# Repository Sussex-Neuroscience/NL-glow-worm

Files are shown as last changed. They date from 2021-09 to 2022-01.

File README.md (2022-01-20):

# GlowWorm_Trackball&LEDstim
A tracking and stimulation system for glow worms

    Authors: A.S.D Fernandes, E. Moubarak, A.M. Chagas & J.E. Niven
    Aknowlegements: M.J.Y. Zimmermann

## Aims
This set-up was designed to investigate male glow-worms attraction to a stimulus that mimics the females' glow. The aim was to be able to do so in tethered animals, whose behavior could be recorded at all times. Furthermore, we intended to have the ability to fully control the stimulus position relative to the glow-worm, as well as other characteristics such as intensity (brightness) and the duration of presentation.

## Methodology

Insects were fixed on top of a walking platform, which consisted in a light polystyrene ball that seated on top of a cup-shaped structure. The cup was perforated at the centre, allowing for air to be pumped through. Thus, the light ball was supported by an air cushion and could, with very little friction, rotate as the glow-worm walked. The movements of the ball, and thus the fictive path of the glow-worm, were recorded by two optical mice sensors, placed close to the ball and orthogonally to each other (Figure 1). The optical mice x and y displacements were recorded by a computer, and were then analyzed in terms of translational and angular distance and velocity. 

The stimulus consisted on LEDs with similar wavelength as the female glow, displayed as an array that surrounded ~ 180° of the insect's lateral visual field. The LEDs were attached to a controller and their intensity and duration of presentation controlled and recorded (Figure 1).

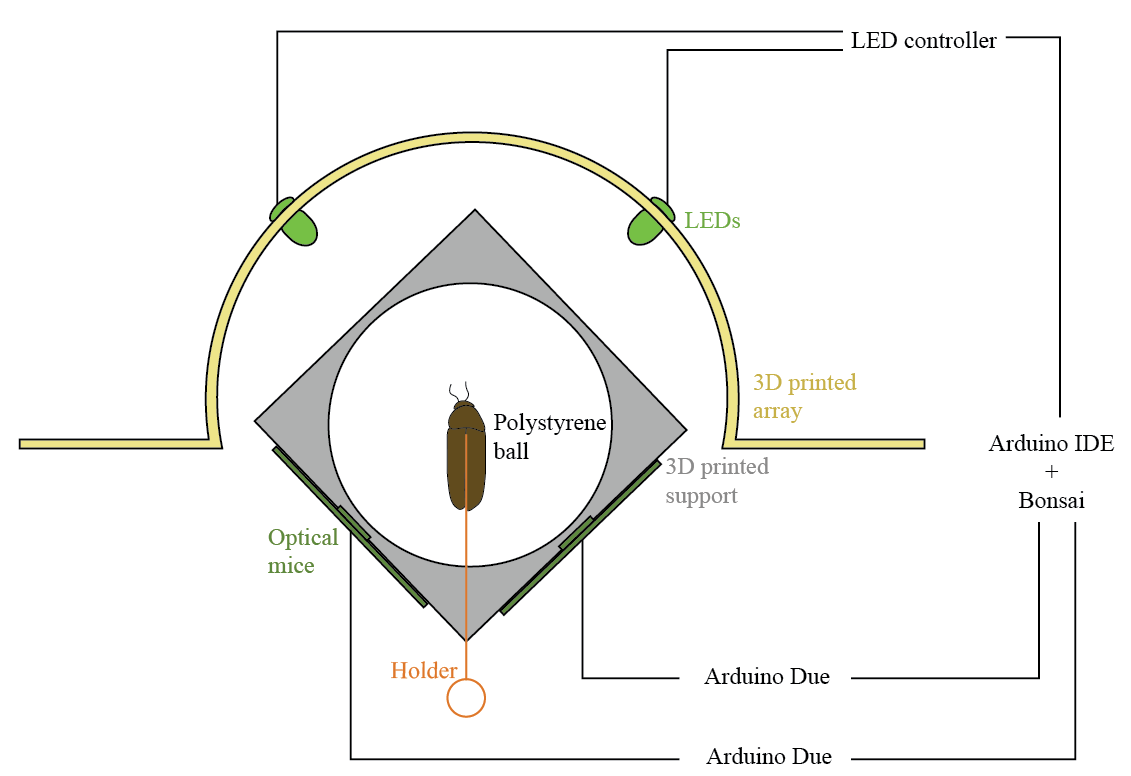
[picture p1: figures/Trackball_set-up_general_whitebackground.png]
Trackball schematics


**Figure 1: Schematics of trackball and stimulation set-up for glow-worms.** A tethered male glow-worm walks on top of a polystyrene ball supported by an air cushion which seats on a custom 3D printed support (gray). As the insect walks, the ball moves beneath it and its movements are recorded by two optical mice sensors (dark green). Each optical mouse is connected to an Arduino Due, in turn connected to a USB port. The glow-worm is presented with light stimuli through LEDs (light green) fixed to a custom 3D printed array (yellow) that surrounds ~ 180° of the insect's lateral visual field. The LEDs are attached to a controller, in turn connected to a USB port. The information from the LEDs and optical mice are recorded with Arduino IDE and saved with Bonsai software.

### Tethering 

Individual male glow-worms were tethered in a fixed position, not being allowed to rotate by themselves on top of the ball nor adjust their height (Figure 2A). The following material was needed for tethering:

- **Tube:** small tube (1.02mm ID, 1.98mm OD, 5mm length) glued to the wings, around the insect's center of mass, with rapid (5 seconds) UV glue. The tube was glued to the glow-worm at all times and attached to the experimental apparatus for experiments.

- **Pipette tip and syringe needle:** cut pipette tip glued to the bent tip of a long syringe needle (length: 120 mm), where the insect's tube could attach to.

- **Micromanipulator:** where the other end of the syringe needle could attach to, for allowing the experimenter to adjust the position and height of the insect on top of the ball.

### Trackball and support

The trackball system was composed of the following materials (Figure 2B,C):

- **Trackball:** polystyrene ball (5 cm diameter).

- **Support:** custom 3D printed structure (Trackball support scad).

- **Pump, regulator, system of tubes and connector:** the air flow was generated by a pump, regulated at about 2-5 lpm, and channeled to the support through a system of tubes of various sizes, ending with a specific connector that fits the model of the support.

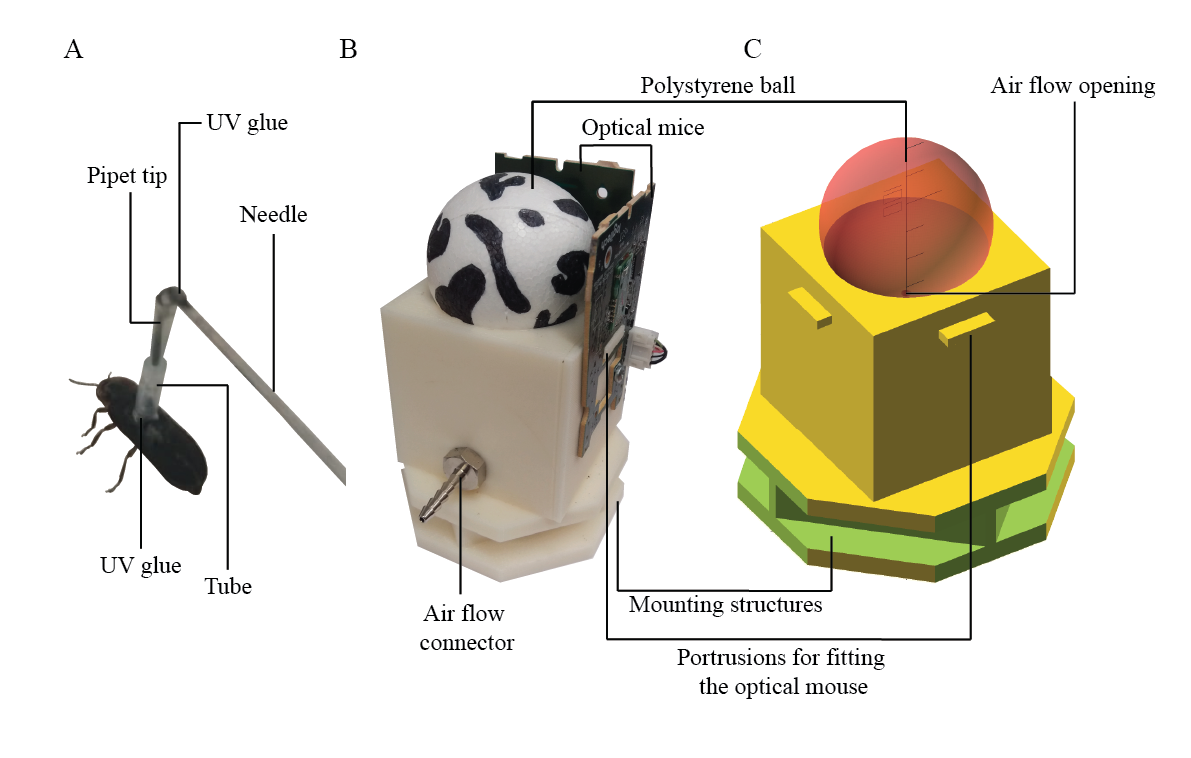
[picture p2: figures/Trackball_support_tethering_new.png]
Trackball support


**Figure 2: Detailed scheme of tethering and trackball support.** A) Male glow-worm with a tube glued to its wings, attached to the pipette tip glued to the bent end of the syringe. The syringe was attached to the micromanipulator for experiments (not shown). B) Photograph and C) Open Scad sketch of the trackball support with the real and fictive ball visible (respectively). The air flow entered through the connector on the side and passed through the opening at the center of the cup. The optical mice were fixed to the support through the portrusions on two ortogonal sides. The indents at the bottom of the support allowed for it to be mounted on a frame that kept it stable (not visible).

### Movement recordings

The walking behaviour of glow-worms was inferred by recordings of the trackball's movement. These recordings were acquired using the following hardware and software:

**Hardware**

- **Optic flow sensors:** two optical mice (M500 Logitech) sensors and relevant circuits were detached from the remaining parts. Each was attached to a side of the trackball support, orthogonal to each other, with the sensor at the level of the ball’s equator (Figure 2B).

- **Arduino Due:** each optical mouse was connected to one Arduino Due, which in turn connected to a USB port on a computer.

**Additional recordings** 

- **Infra-red camera:** placed above the set-up and connected to the same computer via USB (not shown).  

**Software**

- **Arduino IDE (v1.8.15):** for recording the x and y displacements of the optical mice, at ~ 60 fps (Mouse recorder arduino).

- **Bonsai (Lopes et al., 2015):** for saving the information from the Arduinos and camera, with a time stamp per frame, in a .csv file each (Bonsai mouse and cam).

### Stimulus 

A light stimulus was presented to the fixed glow-worm using the following (Figure 3):

**Hardware**

- **LEDs:** wavelength 555 nm; 5 mm diameter.

- **LED array:** custom 3D printed semicircular structure fitting up to 9 LEDs (LED array scad; Figure 3A), placed around the trackball apparatus.

- **LED controller:** custom-printed circuit board which accommodates the microcontroller, the LED driver and up to 24 LED channels (Figure 3B). You can find more detailed information on [BadenLab/LED-Zappelin](https://github.com/BadenLab/LED-Zappelin).

**Software**

- **Arduino IDE (v1.8.15):** for setting and recording the LEDs' intensity and duration (LED array arduino).

- **Bonsai (Lopes et al., 2015):** for saving the LED information and a time stamp per frame in a .csv file (Bonsai LEDs).

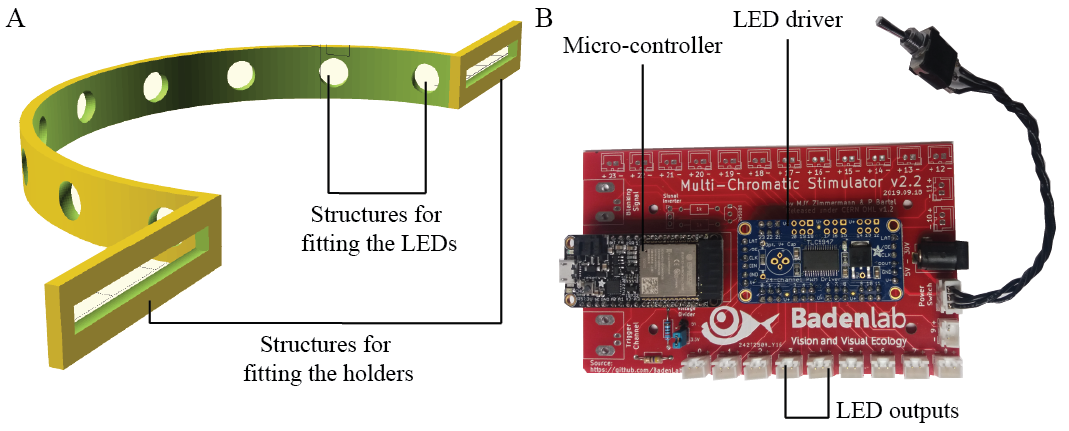
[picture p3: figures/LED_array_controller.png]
LED array and controller


**Figure 3: LED array and controller.** A) custom 3D printed array for fitting LEDs, with two side structures for mounting it on the same frame as the trackball support, arround it (not shown). B) Custom-printed circuit board which accommodates the microcontroller, the LED driver and up to 24 LED channels. 

You can find the detailed list of hardware and software here.

## Data analysis

### Raw variables from the optical mice

The optical mice (Logitech M500) comprise an infrared LED, an image acquisition system (IAS) and a digital signal processor (DSP). The infrared LED light projected onto the trackball surface bounces back and is captured by the IAS, which consists in a sensor that records, in this case, around 60 images per second. As the ball near the mouse moves, these images change and this change is processed by the DPS in order to determine the direction and magnitude of the movement. Thus, the raw data obtained from the optical mice, recorded by the Arduino Due and Bonsai, were:

- **x displacement:** specifies the relative change in pixels (dots/counts) between the current and previous frames, in the horizontal axis;

- **y displacement:** specifies the relative change in pixels (dots/counts) between the current and previous frames, in the vertical axis;

- **Time:** number of microseconds that have passed from the moment the program was uploaded into the Arduino Due.

These raw values were essentially distances, in pixel units, and each frame had an associated time.

### Specific experimental variables

The variable time was normalized to start at zero, converted to seconds (not shown), and used for merging the the data from the two mice to the nearest value. The **time difference** between frames was calculated as the difference between the current frame and the previous. 

For this particular set-up, the insect was tethered on top of the trackball facing a fixed direction. As the animal turned, the ball rotated underneath it and this movement was captured by changes in the horizontal axis of the optical mice sensors. If the animal turned 360 degrees, the ball moved the correspondent value on the opposite direction. Thus, the x displacement values, in pixel units, corresponded to the full perimeter of the ball at the equator level, at which the sensors were placed (Figure 4A).

The variables calculated from the x displacement were:

- **Mean x displacement:** the negative of the mean x displacement value of the two mice;

- **Angular displacement:** Mean x displacement divided by the ball radius and multiplied by 180/pi to obtain the angle in degrees (this also corresponds to instant heading or facing angle);

- **Cumulative angular displacement:** sum of angular displacement of current and all previous frames;

- **x velocity:** Mean x displacement divided by the time difference;

- **Angular velocity:** angular displacement divided by the time difference.

As the insect walked forwards on top of the ball, the movement was captured by the changes in the vertical axis of the optical mice sensors. Because the mice were orthogonal to each other, the y displacement from one mouse (the left) was taken as x and the y displacement from the other mouse as y. The forward velocity was calculated as the hypotenuse between the two sides (Figure 4B). Either mouse's y displacement could correspond to x or y.

The variables calculated from the y displacement were:

- **Forward displacement:** the squared root of the sum of the squared y displacement from one mouse and the squared y displacement of the other;

- **Cumulative forward displacement:** sum of forward displacement of current and all previous frames;

- **Forward velocity:** forward displacement divided by the time difference.

Lastly, the error between the two mice was calculated as the difference between their x displacement values, which should be the same if no error occurred.

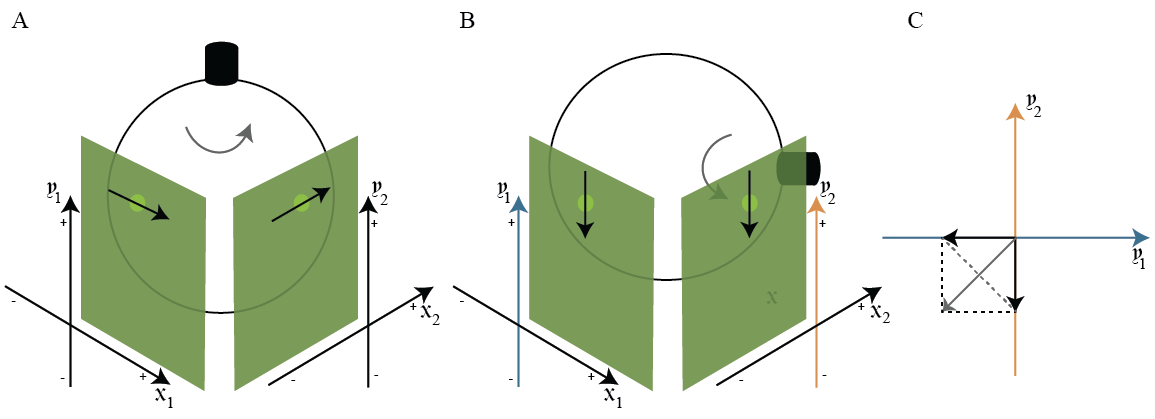
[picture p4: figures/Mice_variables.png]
Mice variables


**Figure 4: Movement direction and corresponding variables from optical mice.** A) Turning movement corresponds to rotation of the ball on the horizontal axis of the optical mice and, consequently, change in their x displacement values. The x displacement from both mice should have the same value if no recording error occured. B) Walking forward corresponds to rotation of the ball on the vertical axis of the optical mice and, consequently, change in their y displacement values. C) The real forward displacement is a combination of the y displacement values from both mice which, because they are ortogonal to each other, can be calculated as the hypotenuse between the two vectors.

## Calibration of the optical mice

### Stepper motor program

The calibration was performed using a stepper motor, controlled by an Arduino Uno. A custom 3D printed ball, of the same diameter of the polystyrene ball (5 cm), was attached to the motor and positioned on top of the trackball support. 

The motor and ball were aligned with the mice to create a fictive reading for:

- rotation on top of the ball (Figure 4A);

- translation forward (axis between the two mice; Figure 4B);

- translation to the left (aligned with the mouse on the right);

- translation to the right (aligned with the mouse on the left).

The motor and ball rotated 360 degrees 15 times, each time with a different speed, for each of the fictive readings.

### Calibration factor

The calibration factor was calculated by dividing the real distance moved, which corresponded to 15 times the perimeter of the ball at the equator (2 * pi * ball radius), by the mouse recorded total distance (x displacement and y displacement).

The calibration factor was very similar between the 4 tests, with a mean of 0.0291947 +/- 7.773015^{-4}.

This value must be multiplied by the x and y displacement from the mouse to get these and remaining variables in real distance and velocity values. This distance is in the unit specified in the ball radius (mm/cm and mm^2/cm^2, respectively).

You can find some semi-edited data from the trackball calibration here.

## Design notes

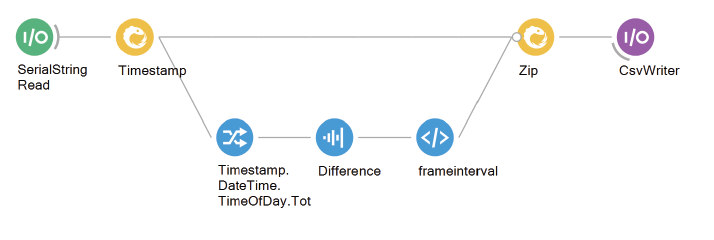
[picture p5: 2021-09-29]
figures/LED_bonsai.png

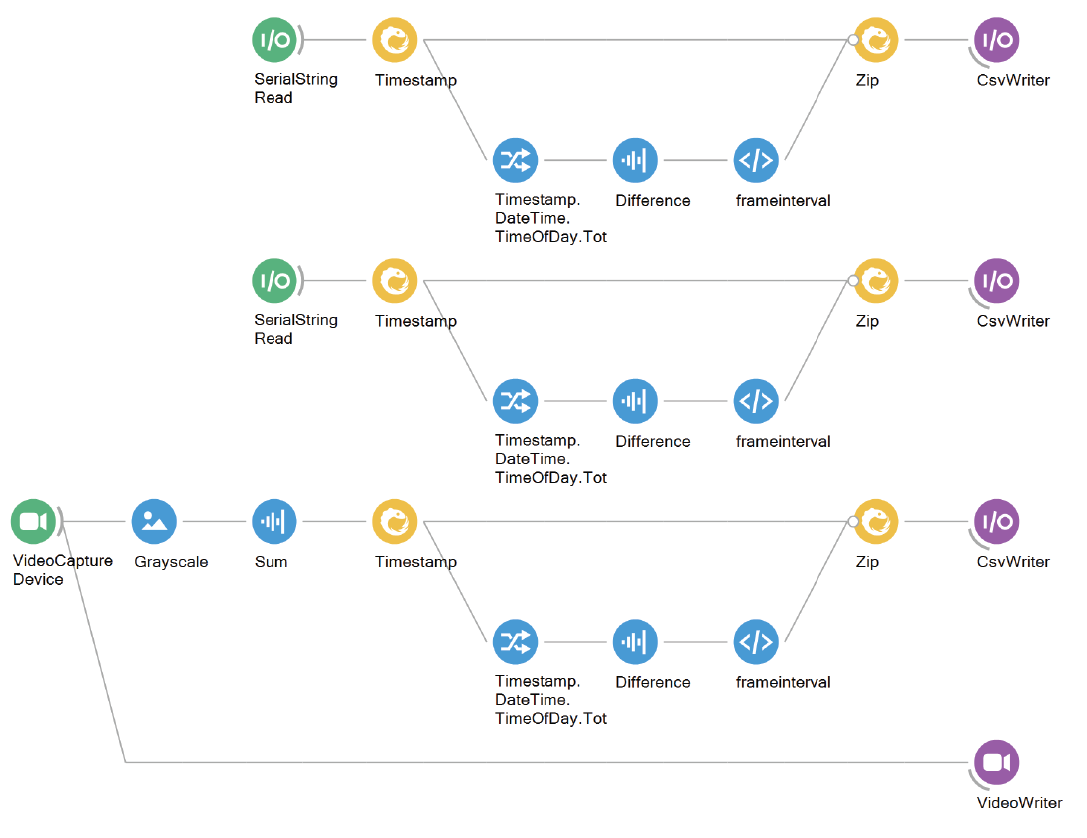
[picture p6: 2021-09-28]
figures/Bonsai_mice_cam.png

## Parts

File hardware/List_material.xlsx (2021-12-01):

Material | Description | Model | Brand | Link
Hardware
Trackball | Polystyrene, 5 cm diameter |  |  | https://ritohobby.co.uk/polystyrene/12200-white-polystyrene-ball-5cm-diameter-1-pcs-5700137321058.html
Trackball support | 3D printed (ABS filament)
Pump | Any with pressure > 10 lpm and constant flow | ET 80 Air Pump | Charles Austen | https://pumpwarehouse.co.uk/shop/charles-austen-et-80-air-pump/
Regulator | Any with pressure ~ 2-5 lpm |  | Futuris | https://www.amazon.co.uk/Futuris-CO2-Welding-Flowmeter-0-30lpm/dp/B01A8L5HYO
Air flow tubes | Any combination that fit the pump, regulator and adaptor
Air flow connector | 8 mm OD | 176-2014 | RS PRO | https://uk.rs-online.com/web/p/hose-connectors/1762014/?searchHistory=%7B%22enabled%22%3Atrue%7D
Optical mouse (2x) | Corded; Infra-red light | M500 | Logitech | https://www.logitech.com/en-us/products/mice/m500s-corded-mouse.910-005783.html
Camera | Infra-red, compatible with PC | ELP-USBFHD05MT-RL36-U | SHENZHEN AILIPU TECNHOLOGY | https://www.amazon.co.uk/gp/product/B015VE6MII/ref=ppx_yo_dt_b_asin_title_o09_s00?ie=UTF8&psc=1
LEDs | Wavelength: 555nm; Size: 5mm diameter | reference SSL-LX5093PGD | Mouser Electronics | https://www.mouser.co.uk/ProductDetail/Lumex/SSL-LX5093PGD?qs=dKJqHdD0tEBZaKNUwnw%2FQg%3D%3D
Arduino Due (2x) |  |  | Arduino | https://uk.rs-online.com/web/p/arduino/7697412/
USB to microUSB cables | Any microUSB male to microUSB male
USB to microUSB connector | Any USB male to microUSB female
Computer | 4 USB ports
LED array | 3D printed semi-circular structure
Microcontroller |  | 3405 | Adafruit Industries LLC | https://www.digikey.co.uk/en/products/detail/adafruit-industries-llc/3405/7244967?s=N4IgTCBcDaIIwFYwA4C0Y7LqgcgERAF0BfIA
LED driver |  | 1429 | Adafruit Industries LLC | https://www.digikey.co.uk/en/products/detail/adafruit-industries-llc/1429/5353645?s=N4IgTCBcDaIIwFYwA4C0c7IagcgERAF0BfIA
Circuit board | Custom-printed |  |  | https://github.com/BadenLab/LED-Zappelin
Frame | 10x10 mm | 100012 | MakerBeam | https://www.makerbeam.com/makerbeam-makerbeam-regular-starter-kit-black.html
Tube for tethering | 1.02mm ID 1.98mm OD | 800/100/300 | Smiths Medical™
Pipet for tethering | 200 ul; Polypropylene | 70.3030.020 | Sarstedt | https://www.sarstedt.com/en/products/laboratory/liquid-handling/pipette-tips/product/70.3030.020/
Syringe needle for tethering | 120 mm length; 0.8 mm OD | 466564/3 | B Braun™ | https://www.fishersci.co.uk/shop/products/stainless-chromium-nickel-steel-light-silicone-coating-needle/10438881
Micromanipulator for tethering | Any that fits the end of the syringe and allows fine adjustments
Software
Arduino IDE |  | Version 1.8.15 | Arduino | https://www.arduino.cc/en/Main/Software_
Bonsai |  |  |  | https://bonsai-rx.org/

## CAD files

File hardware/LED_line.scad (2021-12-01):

// This is a 9 cm diameter semicircular LED array that 
// fits 9 typical LEDs with 5 mm diameter
// equally spaced between each other
// with two holders on the side for attaching it to a frame

echo(version=version());
module LED_line()

// circular array  - 9 cm diameter

difference(){
   difference(){
        difference(){
        cylinder (h = 10, d = 94, $fn=200);
        translate([0, 0, -0.5]){cylinder (h = 11, d = 90, $fn=200);}
        }
        translate([5, -47, -0.5]){cube([120, 120, 120]);}
    }

// holes for LEDs
  // center  
   translate([-46,0,5]){sphere(d = 6, $fn = 50);}

  // side 1 
   translate([-42.498,17.603,5]){sphere(d = 6, $fn = 50);} 
   translate([-32.5269,32.5269,5]){sphere(d = 6, $fn = 50);} 
   translate([-17.603,42.498,5]){sphere(d = 6, $fn = 50);} 
   translate([0,46,5]){sphere(d = 6, $fn = 50);} 
   
  // side 2 
   translate([-42.498,-17.603,5]){sphere(d = 6, $fn = 50);} 
   translate([-32.5269,-32.5269,5]){sphere(d = 6, $fn = 50);} 
   translate([-17.603,-42.498,5]){sphere(d = 6, $fn = 50);} 
   translate([0,-46,5]){sphere(d = 6, $fn = 50);}    
}    

    
// holders    
difference(){
    translate([5,-80.5,0]){cube([2,36,10]);}
    translate([6,-48,5]){rotate([90,0,0]){cylinder(d = 4, h = 30, $fn = 50);}
}}

difference(){
    translate([5,44.5,0]){cube([2,36,10]);}
    translate([6,78,5]){rotate([90,0,0]){cylinder(d = 4, h = 30, $fn = 50);}}
//} 
}










LED_line();

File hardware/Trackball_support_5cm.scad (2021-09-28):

//module TrackBallSupport (h1,r1,z,r2,r3,a,a2,h2,r4,h3){

echo(version=version());
Trackball_support();

module Trackball_support(){



//------- Ball diameter - to change for specific ball size
    ball_diameter = 50;


//------- Other variables - optimized for optical mouse Logitech M500 - do not change unless using different sensor
    ball_to_edge = 5;
    support_cube = ball_diameter + (ball_to_edge*2);
    cup_size = support_cube + (ball_diameter/6);//1/3 of the ball

    mouse_piece_length_out = 5;
    mouse_piece_width = 3;
    mouse_piece_length = 16;
    mouse_to_top = 7;
    
//------- Base - optimized for fitting Makerbeam - do not change unless changing the set-up
    
    beam_width = 12;
    
    base_height = beam_width * 2;
    base_width = support_cube * 1.5;


difference(){ //for inlet

// Trackball support

translate([0,0,base_height]){
     difference(){ 
     difference(){
         translate([-support_cube/2,-support_cube/2,0]){cube(support_cube);}
         #translate([0,0,cup_size]){sphere(d=ball_diameter,$fn=200);} 
     }

 }
 }
 
 
// inlet for pump 
translate([0,0,base_height+10]){ 
 rotate([90,0,0]){
          translate([0,0,support_cube/2-9]){cylinder(h=10,d=9.8,$fn=30);}
          cylinder(h=support_cube/2+1,d=3, $fn=30);
          translate([0,-1.5,0]){rotate([-90,0,0]){cylinder(h=support_cube+1.5,d=3, $fn=30);}}
      }
  }
 }
 

// pieces for fitting mice  
  rotate([0,90,0]){translate([-(support_cube+base_height-mouse_to_top),-mouse_piece_length/2,support_cube/2]){cube([mouse_piece_width,mouse_piece_length,mouse_piece_length_out]);}}
  rotate([0,90,90]){translate([-(support_cube+base_height-mouse_to_top),-mouse_piece_length/2,support_cube/2]){cube([mouse_piece_width,mouse_piece_length,mouse_piece_length_out]);}}

 
// Base

difference(){

rotate([0,0,45]){
    difference(){
    
      translate([-base_width/2,-base_width/2,0]){cube([base_width,base_width,base_height]);}
  
      union(){
          rotate(90,0,0){translate([-(base_width/2),base_width/2-beam_width,beam_width/2]){cube([base_width,beam_width+0.1,beam_width]);}}
          rotate(90,0,0){translate([(-base_width/2),-base_width/2-0.1,beam_width/2]){cube([base_width,beam_width+0.1,beam_width]);}}
          rotate(0,90,0){translate([(-base_width/2),-base_width/2-0.1,beam_width/2]){cube([base_width,beam_width+0.1,beam_width]);}}
         rotate(0,90,0){translate([-(base_width/2),base_width/2-beam_width,beam_width/2]){cube([base_width,beam_width+0.1,beam_width]);}}
      
  }
  }
  }
  translate([-base_width/2,base_width/2,-1]){cube([base_width,base_width,base_height+1.5]);}
  translate([base_width/2,-base_width/2,-1]){cube([base_width,base_width,base_height+1.5]);}
  translate([-base_width*1.5,-base_width/2,-1]){cube([base_width,base_width,base_height+1.5]);}
  translate([-base_width/2,-base_width*1.5,-1]){cube([base_width,base_width,base_height+1.5]);}
} 

}

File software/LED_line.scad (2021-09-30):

// This is a 9 cm diameter semicircular LED array that 
// fits 9 typical LEDs with 5 mm diameter
// equally spaced between each other
// with two holders on the side for attaching it to a frame

echo(version=version());
module LED_line()

// circular array  - 9 cm diameter

difference(){
   difference(){
        difference(){
        cylinder (h = 10, d = 94, $fn=200);
        translate([0, 0, -0.5]){cylinder (h = 11, d = 90, $fn=200);}
        }
        translate([5, -47, -0.5]){cube([120, 120, 120]);}
    }

// holes for LEDs
  // center  
   translate([-46,0,5]){sphere(d = 6, $fn = 50);}

  // side 1 
   translate([-42.498,17.603,5]){sphere(d = 6, $fn = 50);} 
   translate([-32.5269,32.5269,5]){sphere(d = 6, $fn = 50);} 
   translate([-17.603,42.498,5]){sphere(d = 6, $fn = 50);} 
   translate([0,46,5]){sphere(d = 6, $fn = 50);} 
   
  // side 2 
   translate([-42.498,-17.603,5]){sphere(d = 6, $fn = 50);} 
   translate([-32.5269,-32.5269,5]){sphere(d = 6, $fn = 50);} 
   translate([-17.603,-42.498,5]){sphere(d = 6, $fn = 50);} 
   translate([0,-46,5]){sphere(d = 6, $fn = 50);}    
}    

    
// holders    
difference(){
    translate([5,-80.5,0]){cube([2,36,10]);}
    translate([6,-48,5]){rotate([90,0,0]){cylinder(d = 4, h = 30, $fn = 50);}
}}

difference(){
    translate([5,44.5,0]){cube([2,36,10]);}
    translate([6,78,5]){rotate([90,0,0]){cylinder(d = 4, h = 30, $fn = 50);}}
//} 
}










LED_line();

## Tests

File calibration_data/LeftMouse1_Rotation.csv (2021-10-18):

 | LeftMouse1_x | LeftMouse1_y | Time | Time_normalized | Time_normalized_seconds
1 | 0 | 0 | 3868477732 | 0 | 0
2 | 0 | 0 | 3868494372 | 16640 | 0.01664
3 | 0 | 0 | 3868511012 | 33280 | 0.03328
4 | 0 | 0 | 3868527652 | 49920 | 0.04992
5 | 0 | 0 | 3868544292 | 66560 | 0.06656
6 | 0 | 0 | 3868560932 | 83200 | 0.0832
7 | 0 | 0 | 3868577572 | 99840 | 0.09984
8 | 0 | 0 | 3868594212 | 116480 | 0.11648
9 | 0 | 0 | 3868610852 | 133120 | 0.13312
10 | 0 | 0 | 3868627492 | 149760 | 0.14976
11 | 0 | 0 | 3868644132 | 166400 | 0.1664
12 | 0 | 0 | 3868660772 | 183040 | 0.18304
13 | 0 | 0 | 3868677412 | 199680 | 0.19968
14 | 0 | 0 | 3868694052 | 216320 | 0.21632
15 | 0 | 0 | 3868710692 | 232960 | 0.23296
16 | 0 | 0 | 3868727332 | 249600 | 0.2496
17 | 0 | 0 | 3868743972 | 266240 | 0.26624
18 | 0 | 0 | 3868760612 | 282880 | 0.28288
19 | 0 | 0 | 3868777252 | 299520 | 0.29952
20 | 0 | 0 | 3868793892 | 316160 | 0.31616
21 | 0 | 0 | 3868810532 | 332800 | 0.3328
22 | 0 | 0 | 3868827172 | 349440 | 0.34944
23 | 0 | 0 | 3868843812 | 366080 | 0.36608
24 | 0 | 0 | 3868860452 | 382720 | 0.38272
25 | 0 | 0 | 3868877092 | 399360 | 0.39936
26 | 0 | 0 | 3868893732 | 416000 | 0.416
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

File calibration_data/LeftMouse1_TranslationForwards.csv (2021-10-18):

 | LeftMouse1_x | LeftMouse1_y | Time | Time_normalized | Time_normalized_seconds
1 | 0 | 0 | 143813412 | 0 | 0
2 | 0 | 0 | 143829012 | 15600 | 0.0156
3 | 0 | 0 | 143844612 | 31200 | 0.0312
4 | 0 | 0 | 143860212 | 46800 | 0.0468
5 | 0 | 0 | 143875812 | 62400 | 0.0624
6 | 0 | 0 | 143891412 | 78000 | 0.078
7 | 0 | 0 | 143907012 | 93600 | 0.0936
8 | 0 | 0 | 143922612 | 109200 | 0.1092
9 | 0 | 0 | 143938212 | 124800 | 0.1248
10 | 0 | 0 | 143953812 | 140400 | 0.1404
11 | 0 | 0 | 143969412 | 156000 | 0.156
12 | 0 | 0 | 143985012 | 171600 | 0.1716
13 | 0 | 0 | 144000612 | 187200 | 0.1872
14 | 0 | 0 | 144016212 | 202800 | 0.2028
15 | 0 | 0 | 144031812 | 218400 | 0.2184
16 | 0 | 0 | 144047412 | 234000 | 0.234
17 | 0 | 0 | 144063012 | 249600 | 0.2496
18 | 0 | 0 | 144078612 | 265200 | 0.2652
19 | 0 | 0 | 144094212 | 280800 | 0.2808
20 | 0 | 0 | 144109812 | 296400 | 0.2964
21 | 0 | 0 | 144125412 | 312000 | 0.312
22 | 0 | 0 | 144141012 | 327600 | 0.3276
23 | 0 | 0 | 144156612 | 343200 | 0.3432
24 | 0 | 0 | 144172212 | 358800 | 0.3588
25 | 0 | 0 | 144187812 | 374400 | 0.3744
26 | 0 | 0 | 144203412 | 390000 | 0.39
27 | 0 | 0 | 144219012 | 405600 | 0.4056
28 | 0 | 0 | 144234612 | 421200 | 0.4212
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

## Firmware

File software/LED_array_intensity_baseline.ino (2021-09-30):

// Initialise the LED controler
// For more information on the LED controler go to https://github.com/BadenLab/LED-Zappelin

#include <SPI.h>                            // Include the arduino serial port interface library
#include "Adafruit_TLC5947.h"               // Include the Adafruit TLC5947 libvrary. For better result one may change the number of channel defined in the Adafruit_TLC5947.cpp library
#include <SerialCommand.h> //library to tokenize serial commands  

#define   nDriver         1
#define   data           18             // SPI connection, DIN connected to pin MOSI/18
#define   clock           5             // SPI connection, CLK connected to pin SCK/5
#define   latch          21             // SPI connection, LAT connected to pin 21
#define   oe             25            // Optional feature to prevent LED to light up when powering up the TLC board connected to pin A1/DAC1
//const int      pSyncOut      =   26;    // Trigger channel must be connected to pin A0/DAC2
//const int      pBlank        =   36;    // Blanking signal channel must be connected to pin A4/36


SerialCommand sCmd;     // The demo SerialCommand object


Adafruit_TLC5947 tlc = Adafruit_TLC5947(nDriver, clock, data, latch);

int wait=500;

void setup() {
  
  // put your setup code here, to run once:


// Initialise the serial communication with PC
Serial.begin(9600);
// Initialise the Adafruit TLC driver 
tlc.begin();

pinMode(oe, OUTPUT);
digitalWrite(oe, LOW);

 
tlc.write();  
}


// Exemple experiment with two alternating LEDs, increasing in brightness

void loop() {

  int trials = 5;
  const int led_array[] = {4,5}; //LEDs number; note: the board starts counting leds from 0
  int led = led_array[random(0,2)]; //randomize which LED is first to be turned on
  const int brightness[] = {1,10,100,1000,4000}; //brightness levels

 // Print "Ready" at start of the experiment
 // and LED and Brightness = 0
 
      Serial.println("Ready");
      Serial.print(0); 
      Serial.print(";");
      Serial.print(0);
      Serial.print(";");
      Serial.println(micros());

  //turn all leds off
  for (int i=0; i<9; i++){
      tlc.setPWM(i,0);  
    }//end for
  tlc.write();
  delay(1000*60*5);//wait 5 min
      Serial.print(0);
      Serial.print(";");
      Serial.print(0);
      Serial.print(";");
      Serial.println(micros());

  // for loop quick switch + increase intensity every trial    
  for (int i=0; i<trials; i++){
      int bright = brightness[i];

  //turn all leds off
  for (int i=0; i<9; i++){
      tlc.setPWM(i,0);  
    }//end for
  tlc.write();
  
          tlc.setPWM(led,bright);
          tlc.write();
          delay(1000*20);
          Serial.print(led);
          Serial.print(";");
          Serial.print(bright);
          Serial.print(";");
          Serial.println(micros());


  
                if (led == 5) {
                          tlc.setPWM(4,bright);
                          tlc.write();
                           tlc.setPWM(led,0);
                           tlc.write();
                           delay(1000*20);
                            Serial.print(4);
                            Serial.print(";");
                            Serial.print(bright);
                            Serial.print(";");
                            Serial.println(micros());
                      }
                
                    
                      else if (led == 4){

                            tlc.setPWM(5,bright);
                            tlc.write();
                             tlc.setPWM(led,0);
                             tlc.write();
                             delay(1000*20);                            
                              Serial.print(5);
                              Serial.print(";");
                              Serial.print(bright);
                              Serial.print(";");
                              Serial.println(micros());
                      }

}//end for
 
// Turn both LEDs off

  tlc.setPWM(5,0);
  tlc.write();
  tlc.setPWM(4,0);
  tlc.write();
      Serial.print(0);
      Serial.print(";");
      Serial.print(0);
      Serial.print(";");
      Serial.println(micros());
  delay(1000*60);
      Serial.println("Over");
      delay(1000*60*5);

}

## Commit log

2021-04-26 add links and comments on figuring out an optic flow sensor
2021-04-27 #### COMMENTS FROM SOFIA ON OPTICAL SENSOR
2021-04-30 Added trackball support SCAD
    [Trackball_support.scad]
2021-04-30 create folders to organize documentation, remove .ds_store file, add .gitignore to avoid tracking files that are not needed for the project
    [Trackball_support.scad]
2021-05-03 Improved support with space for OF sensors
    [Trackball_support.scad]
2021-05-19 A few hardware updates
    [MakerBeamFootStabilized.scad, MakerBeamFootStabilized.stl, Trackball_support.scad, m3_mount.scad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]
2021-07-02 initial code for the led array using LED Zappelin' system
2021-10-18 Create calibration_data
